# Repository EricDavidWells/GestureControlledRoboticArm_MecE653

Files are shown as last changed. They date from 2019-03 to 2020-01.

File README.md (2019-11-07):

# Realtime Force Myography
Using the gesture controlled robotic arm developed at [HACKED2019](https://github.com/MarkSherstan/HACKED2019) the project advanced to optimize a force myography (FMG) sensor and algorithm package that can be used to robustly control upper limb prosthetics in real time.

## Background
Although there are many multifunctional hands available for prosthesis use, commercial devices are unable to utilize them largely due to restricted control interfaces. Recent research has focused on improving pattern recognition algorithms to decode electromyographic signals (EMG) into multi degree of freedom movements to enable more robust control. Although results are promising in laboratory conditions, this technique has been unable to be transferred into commercial devices. This is largely due to current surface mounted EMG sensors having inherent unpredictable issues that affect the algorithm’s performance such as cross-talk, electrical interference, muscle fatigue effects, perspiration effects, and skin impedance. An alternative to this technology for use in prosthetics is force myography (FMG). This technology seeks to exploit the deformation resulting from residual muscle movement to obtain prosthesis control. This is typically done in a very similar manner to EMG; however, instead of measuring electrical activity, an array of pressure sensors wrapped around the user’s arm measures muscle deformation. The measured sensor values act as inputs into a pattern recognition algorithm to predict the desired motions from the user. An FMG sensor and algorithm package was designed and optimized to implement robust, real time control of a simulated prosthetic device. Two iterations of prototyping have been achieved, with the second design resulting in a wireless, low profile wristband containing 11 force sensitive resistors (FSR) sensors and an inertial measurement unit (IMU) capable of sampling up to 200 Hz.

## Photos
### Wireless Armband with 11 FSR's, IMU, and Custom PCB
<p align="center">


### Coordinate Frame on Arm
<p align="center">


### Gestures
<p align="center">


### Raw Signals (Left Time Series - Right Spectral Series)
<p align="center">


### Classified Signals PCA Representation 
<p align="center">


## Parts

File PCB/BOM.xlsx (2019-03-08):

Designator | Value | Manufacturer Part # | DIGI-KEY Part # | Rqd Qty | Cost / Unit | x Extra | Total Qty | Total Cost | Notes | Link
R1,R2,R3,R4,R5,R6,R7,R8 | 5.1 k | ERJ-3EKF5101V | P5.10KHCT-ND | 8 | $0.10 | 5 | 40 | $3.92 | Price Break! | https://www.digikey.ca/product-detail/en/ERJ-3EKF5101V/P5.10KHCT-ND
R9 | 1 k | ERJ-3EKF1001V | P1.00KHCT-ND | 1 | $0.10 | 10 | 10 | $0.98 | Price Break! | https://www.digikey.ca/product-detail/en/ERJ-3EKF1001V/P1.00KHCT-ND
R10 | 2 k | ERJ-3EKF2001V | P2.00KHCT-ND | 1 | $0.10 | 10 | 10 | $0.98 | Price Break! | https://www.digikey.ca/product-detail/en/ERJ-3EKF2001V/P2.00KHCT-ND
R11,R12,R13,R14,R15,R16 | 10 k | ERJ-3EKF1002V | P10.0KHCT-ND | 6 | $0.10 | 7 | 42 | $4.12 | Price Break! | https://www.digikey.ca/product-detail/en/ERJ-3EKF1002V/P10.0KHCT-ND
C1,C2,C3 | 0.1 uF | CL10B104KB8NNNC | 1276-1000-1-ND | 3 | $0.05 | 7 | 21 | $0.99 | Price Break! | https://www.digikey.ca/product-detail/en/CL10B104KB8NNNC/1276-1000-1-ND
C4 | 2.2 nF | CL10B222JB8NNNC | 1276-1987-1-ND | 1 | $0.06 | 10 | 10 | $0.60 | Price Break! | https://www.digikey.ca/product-detail/en/CL10B222JB8NNNC/1276-1987-1-ND
C5 | 10 nF | CL10B103KB8NNNC | 1276-1009-1-ND | 1 | $0.05 | 10 | 10 | $0.52 | Price Break! | https://www.digikey.ca/product-detail/en/CL10B103KB8NNNC/1276-1009-1-ND
Q1,Q2 | - | BSS138 | BSS138CT-ND | 2 | $0.40 | 5 | 10 | $3.96 | Price Break! | https://www.digikey.ca/product-detail/en/on-semiconductor/BSS138/BSS138CT-ND/244294
U1 | - | 74HC4051BQ,115 | 1727-6049-1-ND | 1 | $0.59 | 10 | 10 | $5.88 | Price Break! | https://www.digikey.ca/product-detail/en/nexperia-usa-inc/74HC4051BQ115/1727-6049-1-ND/2753885
U2 | - | MPU-6050 | 1428-1007-1-ND | 1 | $11.01 | 5 | 5 | $55.04 | Price Break! | https://www.digikey.ca/product-detail/en/tdk-invensense/MPU-6050/1428-1007-1-ND/4038010
 |  |  |  |  |  |  | Total | $76.98
Other | Qty | Cost / Unit | Total Cost | Link
MPU 6050 Breakout | 1 | $14.47 | $14.47 | https://www.digikey.ca/product-detail/en/dfrobot/SEN0142/1738-1070-ND/6588492
Stepper Motor Driver | 2 | $12.05 | $24.10 | https://www.digikey.ca/product-detail/en/trinamic-motion-control-gmbh/TMC-SILENTSTEPSTICK/1460-1159-ND/5724190
Motor Controller / PDB | 1 | $30.13 | $30.13 | https://www.digikey.ca/product-detail/en/trinamic-motion-control-gmbh/TMC2660-BOB/1460-1245-ND/8037672
 |  | Total | $68.70
$100 Free Shipping
10^-6 micro µ | 0.0022 pF
10^-9 nano n | 2.2 nF
10^-12 pico p | 2200 uF

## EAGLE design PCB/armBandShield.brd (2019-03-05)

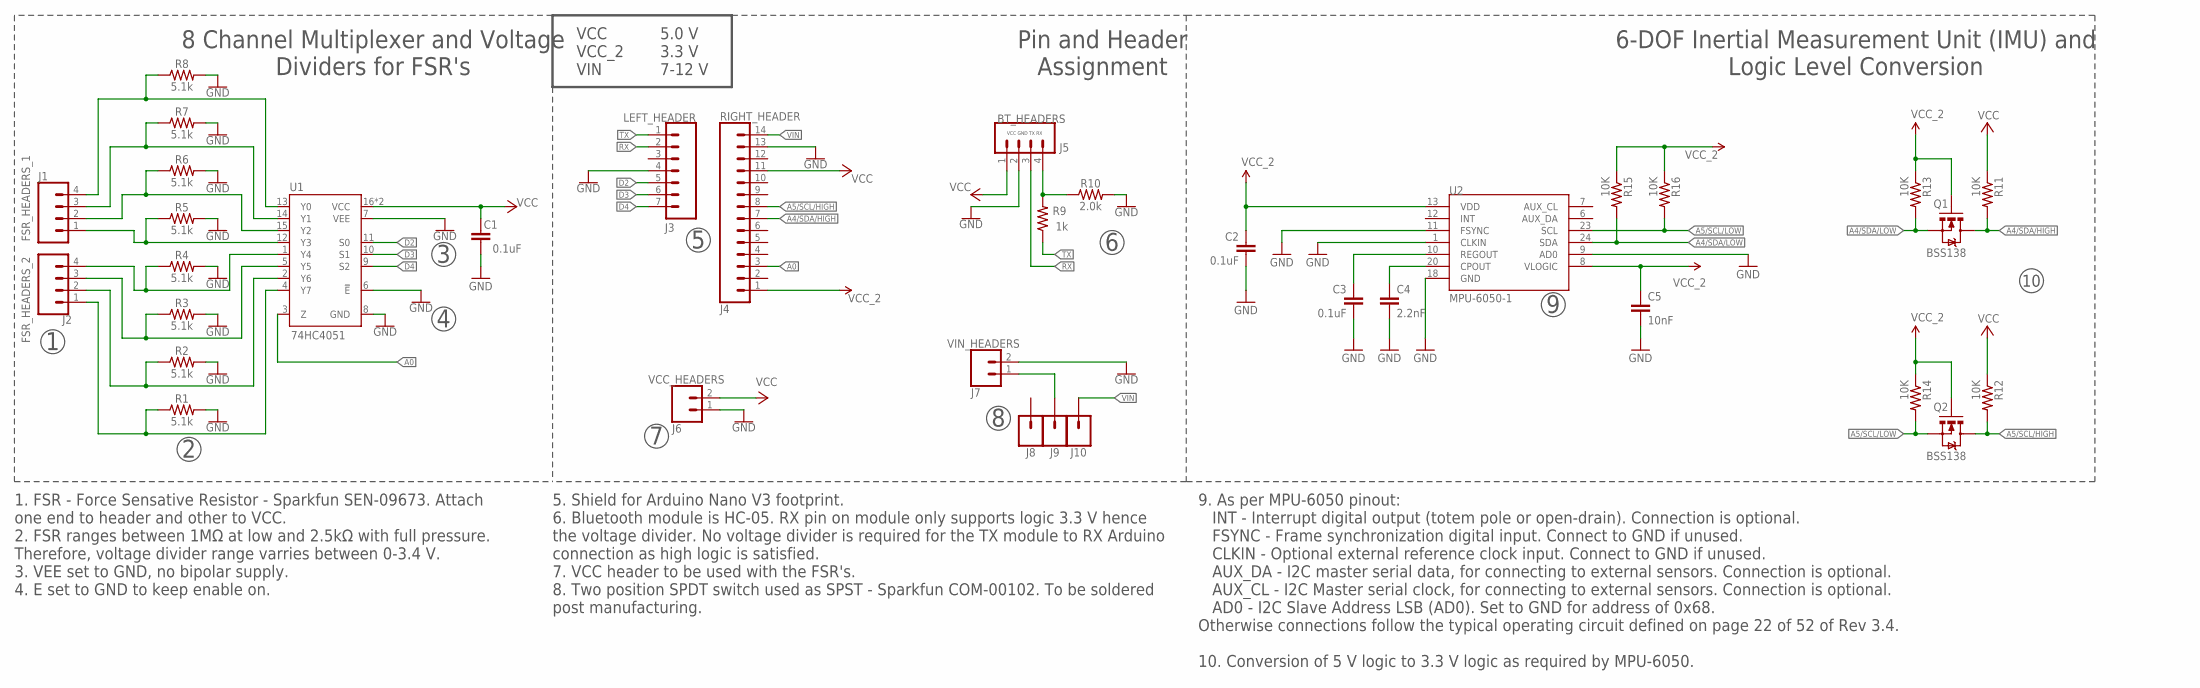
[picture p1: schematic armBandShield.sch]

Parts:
74HC4051: U1; DHVQFN-16-2.5X3.5MM
BT_HEADERS: J5; 1X04
C1, C2, C3: 0.1uF; 0603-CAP
C4: 2.2nF; 0603
C5: 10nF; 0603
J1: FSR_HEADERS_1; 1X04
J2: FSR_HEADERS_2; 1X04
J8, J9, J10: CONN_01; 1X01
LEFT_HEADER: J3; 1X07
Q1, Q2: BSS138; SOT23-3
R1, R2, R3, R4, R5, R6, R7, R8: 5.1k; 0603
R9: 1k; 0603
R10: 2.0k; 0603
R11, R12, R13, R14, R15, R16: 10K; 0603-RES
RIGHT_HEADER: J4; 1X14
U2: MPU-6050-1; QFN-24-4MM2
VCC_HEADERS: J6; 1X02_LONGPADS
VIN_HEADERS: J7; 1X02_LONGPADS

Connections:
A0: 74HC4051.3 (Z), RIGHT_HEADER.3
A4/SDA/HIGH: Q1.3 (D), R11.2, RIGHT_HEADER.7
A4/SDA/LOW: Q1.2 (S), R13.2, R15.2, U2.24 (SDA)
A5/SCL/HIGH: Q2.3 (D), R12.2, RIGHT_HEADER.8
A5/SCL/LOW: Q2.2 (S), R14.2, R16.2, U2.23 (SCL)
D2: 74HC4051.11 (S0), LEFT_HEADER.5
D3: 74HC4051.10 (S1), LEFT_HEADER.6
D4: 74HC4051.9 (S2), LEFT_HEADER.7
FSR1: 74HC4051.4 (Y7), J2.1, R1.1
FSR2: 74HC4051.2 (Y6), J2.2, R2.1
FSR3: 74HC4051.5 (Y5), J2.3, R3.1
FSR4: 74HC4051.1 (Y4), J2.4, R4.1
FSR5: 74HC4051.12 (Y3), J1.1, R5.1
FSR6: 74HC4051.15 (Y2), J1.2, R6.1
FSR7: 74HC4051.14 (Y1), J1.3, R7.1
FSR8: 74HC4051.13 (Y0), J1.4, R8.1
GND: 74HC4051.6 (!E!), 74HC4051.7 (VEE), 74HC4051.8 (GND), BT_HEADERS.2, C1.2, C2.2, C3.2, C4.2, C5.2, LEFT_HEADER.4, R1.2, R2.2, R3.2, R4.2, R5.2, R6.2, R7.2, R8.2, R10.2, RIGHT_HEADER.13, U2.1 (CLKIN), U2.9 (AD0), U2.11 (FSYNC), U2.18 (GND), VCC_HEADERS.1, VIN_HEADERS.2
unnamed: J9.1, VIN_HEADERS.1
unnamed: C4.1, U2.20 (CPOUT)
unnamed: C3.1, U2.10 (REGOUT)
unnamed: BT_HEADERS.4, R9.2, R10.1
RX: BT_HEADERS.3, LEFT_HEADER.2
TX: LEFT_HEADER.1, R9.1
VCC: 74HC4051.16 (VCC), 74HC4051.EP (VCC), BT_HEADERS.1, C1.1, R11.1, R12.1, RIGHT_HEADER.11, VCC_HEADERS.2
VCC_2: C2.1, C5.1, Q1.1 (G), Q2.1 (G), R13.1, R14.1, R15.1, R16.1, RIGHT_HEADER.1, U2.8 (VLOGIC), U2.13 (VDD)
VIN: J10.1, RIGHT_HEADER.14

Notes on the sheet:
VCC GND TX RX
8 Channel Multiplexer and Voltage Dividers for FSR's
1. FSR - Force Sensative Resistor - Sparkfun SEN-09673. Attach one end to header and other to VCC. 2. FSR ranges between 1MΩ at low and 2.5kΩ with full pressure. Therefore, voltage divider range varries between 0-3.4 V. 3. VEE set to GND, no bipolar supply. 4. E set to GND to keep enable on.
Pin and Header Assignment
6-DOF Inertial Measurement Unit (IMU) and Logic Level Conversion
5. Shield for Arduino Nano V3 footprint. 6. Bluetooth module is HC-05. RX pin on module only supports logic 3.3 V hence the voltage divider. No voltage divider is required for the TX module to RX Arduino connection as high logic is satisfied. 7. VCC header to be used with the FSR's. 8. Two position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
VCC VCC_2 VIN
5.0 V 3.3 V 7-12 V
9. As per MPU-6050 pinout: INT - Interrupt digital output (totem pole or open-drain). Connection is optional. FSYNC - Frame synchronization digital input. Connect to GND if unused. CLKIN - Optional external reference clock input. Connect to GND if unused. AUX_DA - I2C master serial data, for connec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

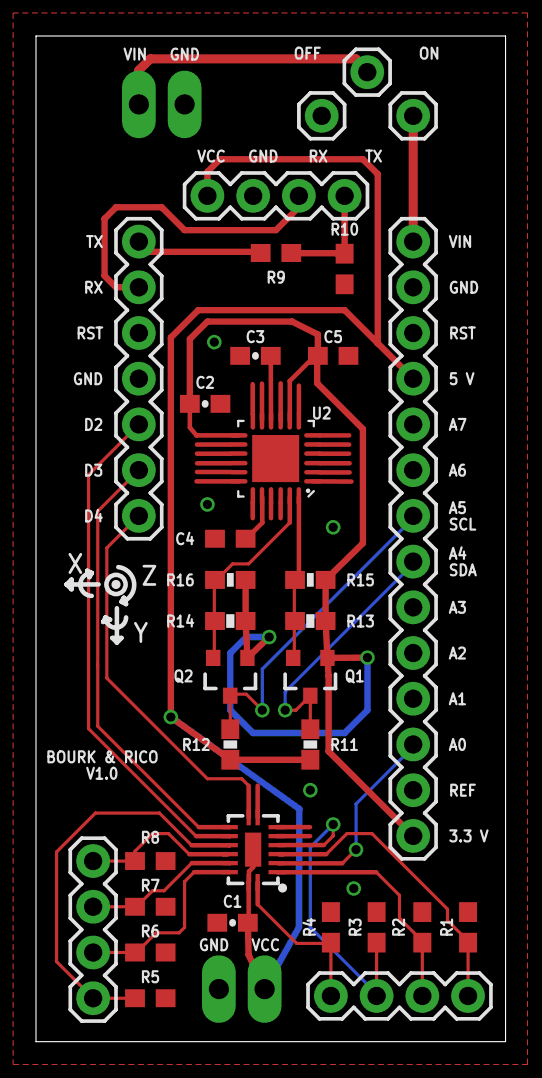
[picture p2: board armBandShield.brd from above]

Board: 2 copper layers, 26.1 x 55.9 mm, 35 parts (0 on the bottom side), 26 nets.

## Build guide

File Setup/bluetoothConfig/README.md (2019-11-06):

# Raspberry Pi 3B+ and HC-05 Set Up and Pairing

## Intro
The initial setup took a couple of hours of fiddling around with different methods and packages. The final working version was heavily based on u/Illmatic-Herbicide's [post on reddit](https://www.reddit.com/r/raspberry_pi/comments/6nchaj/guide_how_to_establish_bluetooth_serial/), however a few steps and other minor additions were made which are documented below.

The `bluetoothConfig.ino` is for setting up the HC-05 baud rate, name, etc... using AT commands. Doccumentation can be found at the begging of the sketch for proper connections, commands, etc...

## Notes
* This is specifically a headless approach and it is assumed the user has SSH'd into their Pi.
* `ratom` can be replaced by `nano` or any other text editor being used.
* When running `[bluetooth]#` enter `help` at any point for a full list of commands and explanations.
* This guide will be updated if further information is found or guidance is requested.

## Instructions
Upgrade all packages and get the required packages.
```
sudo apt-get dist-upgrade
sudo apt-get update
sudo apt-get upgrade
sudo apt-get install bluez pi-bluetooth python-bluez
```

Enter the following command for configuring Bluetooth devices (specifically on Linux).
```
bluetoothctl
```

The next 2 commands will accomplish:
1. Turn on RPi bluetooth if its not already
2. Scan for devices
```
[bluetooth]# power on
[bluetooth]# scan on
```
After waiting for a few seconds the device should be found. For example mine looked similar to this:
```
[bluetooth]#  scan on
    ...
    Device 98:D3:71:FD:61:63 Name: MECE653
    ...
```
The unique address `98:D3:71:FD:61:63` is equal to `<dev>` below. Set `<dev>` to your devices address in the remaining steps if different. Again, `<dev>` will be in the form of XX:XX:XX:XX:XX:XX.

Once your specific device has been found enter the remaining commands which do the following:
1. Stop scanning for devices
2. Enable agent with given capability
3. Pair with device. **You may need to enter a pin at this step!**
4. Trust the device
5. Connect to the device
6. Look at the device and ensure it is paired, trusted, and connected.
```
[bluetooth]# scan off
[bluetooth]# agent on
[bluetooth]# pair <dev>
[bluetooth]# trust <dev>
[bluetooth]# connect <dev>
[bluetooth]# info <dev>
```

Edit the following file using `sudo ratom /etc/systemd/system/dbus-org.bluez.service` and add "-C" to the **ExecStart** line. Then add a new line directly below it and copy and paste **ExecStartPost=/usr/bin/sdptool add SP**. The file will look something like this:

```
...
ExecStart=/usr/lib/bluetooth/bluetoothd -C
ExecStartPost=/usr/bin/sdptool add SP
...
```

Then edit the following file using `sudo ratom /etc/bluetooth/rfcomm.conf` to match the following information:
```
rfcomm1 {
    # Automatically bind the device at startup
    bind yes;

    # Bluetooth address of the device
    device <dev>;

    # RFCOMM channel for the connection
    channel 1;

    # Description of the connection
    comment "My Bluetooth Connection";
}
```

Reboot RPi using `sudo reboot` and SSH back in. Try running:

```
sudo rfcomm bind /dev/rfcomm0 <dev> 1
```

If you do not get any errors and everything checks out go ahead to `main.py` and give it a try. The Bluetooth serial port will be on `/dev/rfcomm0`.

If I missed any steps or something is not working please leave a comment or issue so that the guide can be fixed. A good resource can be found [here](https://www.raspberrypi.org/forums/viewtopic.php?t=188295).

## Update
Once everything is set up properly when logging onto the RPi simply enter the command below to activate the bluetooth serial port.

```
sudo rfcomm bind /dev/rfcomm0 98:D3:71:FD:61:63 1
```

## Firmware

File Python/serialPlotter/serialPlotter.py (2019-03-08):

# Adapted from https://www.thepoorengineer.com/en/arduino-python-plot/
from threading import Thread
import serial
import time
import collections
import matplotlib.pyplot as plt
import matplotlib.animation as animation
import struct
import copy
import pandas as pd


class serialPlot:
    def __init__(self, serialPort='/dev/cu.usbmodem14201', serialBaud=38400, plotLength=100, dataNumBytes=2, numPlots=1):
        self.port = serialPort
        self.baud = serialBaud
        self.plotMaxLength = plotLength
        self.dataNumBytes = dataNumBytes
        self.numPlots = numPlots
        self.rawData = bytearray(numPlots * dataNumBytes)
        self.dataType = None
        if dataNumBytes == 2:
            self.dataType = 'h'     # 2 byte integer
        elif dataNumBytes == 4:
            self.dataType = 'f'     # 4 byte float
        self.data = []
        for i in range(numPlots):   # give an array for each type of data and store them in a list
            self.data.append(collections.deque([0] * plotLength, maxlen=plotLength))
        self.isRun = True
        self.isReceiving = False
        self.thread = None
        self.plotTimer = 0
        self.previousTimer = 0
        # self.csvData = []

        print('Trying to connect to: ' + str(serialPort) + ' at ' + str(serialBaud) + ' BAUD.')
        try:
            self.serialConnection = serial.Serial(serialPort, serialBaud, timeout=4)
            print('Connected to ' + str(serialPort) + ' at ' + str(serialBaud) + ' BAUD.')
        except:
            print("Failed to connect with " + str(serialPort) + ' at ' + str(serialBaud) + ' BAUD.')

    def readSerialStart(self):
        if self.thread == None:
            self.thread = Thread(target=self.backgroundThread)

            self.thread.start()
            # Block till we start receiving values
            while self.isReceiving != True:
                time.sleep(0.1)

    def getSerialData(self, frame, lines, lineValueText, lineLabel, timeText):
        currentTimer = time.perf_counter()
        self.plotTimer = int((currentTimer - self.previousTimer) * 1000)     # the first reading will be erroneous
        self.previousTimer = currentTimer
        timeText.set_text('Plot Interval = ' + str(self.plotTimer) + ' ms')
        privateData = copy.deepcopy(self.rawData[:])    # so that the 3 values in our plots will be synchronized to the same sample time
        for i in range(self.numPlots):
            data = privateData[(i*self.dataNumBytes):(self.dataNumBytes + i*self.dataNumBytes)]
            value,  = struct.unpack(self.dataType, data)
            self.data[i].append(value)    # we get the latest data point and append it to our array
            lines[i].set_data(range(self.plotMaxLength), self.data[i])
            lineValueText[i].set_text('[' + lineLabel[i] + '] = ' + str(value))
        # self.csvData.append([self.data[0][-1], self.data[1][-1], self.data[2][-1]])

    def backgroundThread(self):    # retrieve data
        time.sleep(1.0)  # give some buffer time for retrieving data
        self.serialConnection.reset_input_buffer()
        self.serialConnection.timeout = 0

        # print(self.serialConnection._timeout)
        self.serialConnection.read(16*20)
        # print(self.rawData)
        self.serialConnection.timeout = None
        # print(self.serialConnection._timeout)

        while (self.isRun):
            self.serialConnection.readinto(self.rawData)
            self.isReceiving = True
            # print(self.rawData)

    def close(self):
        self.isRun = False
        self.thread.join()
        self.serialConnection.close()
        print('Disconnected...')
        # df = pd.DataFrame(self.csvData)
        # df.to_csv('../Desktop/data.csv')

å
def main():
    # portName = 'COM5'
    portName = '/dev/cu.usbmodem14201'
    baudRate = 115200
    maxPlotLength = 100     # number of points in x-axis of real time plot
    dataNumBytes = 2        # number of bytes of 1 data point
    numPlots = 8            # number of plots in 1 graph

    s = serialPlot(portName, baudRate, maxPlotLength, dataNumBytes, numPlots)
    s.readSerialStart()

    # plotting starts below
    pltInterval = 20    # Period at which the plot animation updates [ms]
    xmin = 0
    xmax = maxPlotLength
    ymin = 0
    ymax = 1024

    fig = plt.figure(figsize=(12, 6))
    ax = plt.axes(xlim=(xmin, xmax), ylim=(float(ymin - (ymax - ymin) / 10), float(ymax + (ymax - ymin) / 10)))
    ax.set_title("FSR Live Output",fontweight='bold',size=20)
    ax.set_xlabel("Time -->",fontweight='bold')
    ax.set_ylabel("Raw Analog Out",fontweight='bold')

    lineLabel = ['FSR1', 'FSR2', 'FSR3', 'FSR4', 'FSR5', 'FSR6', 'FSR7', 'FSR8']
    style = ['c-', 'm-', 'y-', '-k', '--c', '--m', '--y', '--k']
    timeText = ax.text(0.80, 0.95, '', transform=ax.transAxes)
    lines = []
    lineValueText = []
    for i in range(numPlots):
        lines.append(ax.plot([], [], style[i], label=lineLabel[i])[0])
        lineValueText.append(ax.text(0.05, 0.95-i*0.05, '', transform=ax.transAxes))

    anim = animation.FuncAnimation(fig, s.getSerialData, fargs=(lines, lineValueText, lineLabel, timeText), interval=pltInterval)    # fargs has to be a tuple

    plt.legend(loc='upper center', ncol=4)
    plt.xticks([])
    plt.show()

    s.close()


if __name__ == '__main__':
    main()

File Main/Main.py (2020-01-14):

from scipy.stats import mode
from threading import Thread
from sklearn import svm
import pandas as pd
import numpy as np
import serial
import struct
import time
import queue
import math
import pickle
import platform
import matplotlib.animation as animation


if platform.system() == "Windows":
    COMPORT = "COM16"
    import cv2
    from sklearn.decomposition import PCA
    from matplotlib import pyplot as plt
    from mpl_toolkits import mplot3d
elif platform.system() == "Darwin":
    COMPORT = "/dev/cu.MECE653-DevB"
    import cv2
    from sklearn.decomposition import PCA
    from matplotlib import pyplot as plt
    from mpl_toolkits import mplot3d
else:
    COMPORT = "/dev/rfcomm0"
    import RPi.GPIO as GPIO


class Model:
    def __init__(self, model=None):
        self.model = model
        self.trainingxdata = None
        self.trainingydata = None

    def get_training_data(self, q, data, n, classnum, trainnum):
        xdata = []
        ydata = []
        counter = 0
        for i in range(0, trainnum):
            print("Training iteration: {0}".format(i))
            for k in range(0, classnum):
                print("Class number: {0} starting in 1 second..".format(k))
                time.sleep(2)
                print("Getting data")
                # input("press enter")
                q.empty()
                for j in range(0, n):
                    data.getData(q)
                    a = [int(x) for x in data.force]
                    # b = [int(data.ax),int(data.ay),int(data.az),int(data.gx),int(data.gy),int(data.gz),int(data.dtTimer)]
                    # c = a+b
                    xdata.append(a)
                    ydata.append(k)

        self.trainingxdata = np.array(xdata)
        self.trainingydata = np.array(ydata)

    def plot_pca(self, show=True):
        self.pca = PCA(n_components=3)
        self.pca.fit(self.trainingxdata)
        Xpca = self.pca.fit_transform(self.trainingxdata)

        ax = plt.axes(projection='3d')
        for i in range(0, int(self.trainingydata.max()) + 1):
            Xtemp = Xpca[self.trainingydata == i]
            ax.scatter3D(Xtemp[:, 0], Xtemp[:, 1], Xtemp[:, 2], cmap='Greens')
            # ax.scatter3D(Xtemp[0::100][:, 0], Xtemp[0::100][:, 1], Xtemp[0::100][:, 2], cmap='Greens')
            ax.set_xlabel("PCA Axis 1")
            ax.set_ylabel("PCA Axis 2")
            ax.set_zlabel("PCA Axis 3")

        if show is True:
            plt.figure(1)
            plt.show()

    def trainSVM(self):
        self.model = svm.SVC(kernel='rbf', gamma='scale')
        self.model.fit(self.trainingxdata, self.trainingydata)

    def predict(self, data):
        prediction = self.model.predict([data])
        return prediction

    def score(self, xdata, ydata):
        score = self.model.score(xdata, ydata)
        return score

    def savemodel(self, filename):
        pickle.dump(self, open(filename, 'wb'))

    def data_split(self, p):
        """
        splits data into training and testing data by percentage p.
        :param data: ndarray of total data to be split
        :param p: percentage of data to be used for training
        :return: data split into training and testing
        """

        data = np.hstack((self.trainingxdata, np.transpose(np.array([self.trainingydata]))))
        datashuff = np.array(data)
        np.random.shuffle(datashuff)

        cutoff = int(p * data.shape[0])
        self.trainingxdata = datashuff[0:cutoff, 0:-1]
        self.trainingydata = datashuff[0:cutoff, -1]

        self.testingxdata = datashuff[cutoff::, 0:-1]
        self.testingydata = datashuff[cutoff::, -1]


class Sensors:
    def __init__(self, gyroScaleFactor, accScaleFactor, VCC, Resistor, tau):
        # Class / object / constructor setup
        self.gyroScaleFactor = gyroScaleFactor
        self.accScaleFactor = accScaleFactor
        self.VCC = VCC
        self.Resistor = Resistor
        self.tau = tau

        self.gx = None; self.gy = None; self.gz = None;
        self.ax = None; self.ay = None; self.az = None;

        self.gyroXcal = 0
        self.gyroYcal = 0
        self.gyroZcal = 0

        self.gyroRoll = 0
        self.gyroPitch = 0
        self.gyroYaw = 0

        self.roll = 0
        self.pitch = 0
        self.yaw = 0

        self.dtTimer = 0

        self.FSRvalues = []
        self.force = [0, 0, 0, 0, 0, 0, 0, 0, 0, 0, 0, 0]

    def getRawSensorValues(self, q):
        # Get raw values from serial connection
        while q.empty():
            time.sleep(0.0001)
            pass
        val = q.get(block=False)
        q.task_done()

        self.gx = val[0]
        self.gy = val[1]
        self.gz = val[2]
        self.ax = val[3]
        self.ay = val[4]
        self.az = val[5]
        self.FSRvalues = [val[6], val[7], val[8], val[9], val[10], val[11], val[12], val[13], val[14], val[15], val[16]]

    def calibrateGyro(self, s, N):
        # Display message
        print("Calibrating gyro with " + str(N) + " points. Do not move!")

        # Take N readings for each coordinate and add to itself
        for ii in range(N):
            self.getRawSensorValues(s)
            self.gyroXcal += self.gx
            self.gyroYcal += self.gy
            self.gyroZcal += self.gz

        # Find average offset value
        self.gyroXcal /= N
        self.gyroYcal /= N
        self.gyroZcal /= N

        # Display message and restart timer for comp filter
        print("Calibration complete")
        self.dtTimer = time.time()

    def processIMUvalues(self):
        # Subtract the offset calibration values
        self.gx -= self.gyroXcal
        self.gy -= self.gyroYcal
        self.gz -= self.gyroZcal

        # Convert to instantaneous degrees per second
        self.gx /= self.gyroScaleFactor
        self.gy /= self.gyroScaleFactor
        self.gz /= self.gyroScaleFactor

        # Convert to g force
        self.ax /= self.accScaleFactor
        self.ay /= self.accScaleFactor
        self.az /= self.accScaleFactor

    def compFilter(self):
        # Get the processed values from IMU
        self.processIMUvalues()

        # Get delta time and record time for next call
        dt = time.time() - self.dtTimer
        self.dtTimer = time.time()

        # Acceleration vector angle
        accPitch = math.degrees(math.atan2(self.ay, self.az))
        accRoll = math.degrees(math.atan2(self.ax, self.az))

        # Gyro integration angle
        self.gyroRoll -= self.gy * dt
        self.gyroPitch += self.gx * dt
        self.gyroYaw += self.gz * dt
        self.yaw = self.gyroYaw

        # Comp filter
        self.roll = (self.tau)*(self.roll - self.gy*dt) + (1-self.tau)*(accRoll)
        self.pitch = (self.tau)*(self.pitch + self.gx*dt) + (1-self.tau)*(accPitch)

    def processFSRvalues(self):
        # Loop through all values
        for ii in range(len(self.FSRvalues)):
            # Analog value to voltage
            fsrV = self.FSRvalues[ii] * self.VCC / 1023.0

            # Use voltage and static resistor value to calculate FSR resistance
            try:
                fsrR = ((self.VCC - fsrV) * self.Resistor) / fsrV
            except:
                fsrR = 1e6

            # Guesstimate force based on slopes in figure 3 of FSR datasheet (conductance)
            fsrG = 1.0 / fsrR

            # Break parabolic curve down into two linear slopes
            if (fsrR <= 600):
                self.force[ii] = (fsrG - 0.00075) / 0.00000032639
            else:
                self.force[ii] =  fsrG / 0.000000642857

        # Write the last entry of force to be the average value
        self.force[11] = np.mean(self.force)

    def getData(self, s):
        # Get current time
        timer = time.perf_counter()

        # Stabilize sampling rate to 200 Hz
        while (time.perf_counter() < timer + 0.005):
            pass

        # Get data from serial
        self.getRawSensorValues(s)

        # Process IMU values
        self.compFilter()

        # Process FSR values
        self.processFSRvalues()

    def logData(self, s, T):
        # Set up timer, counter, and temp data storage
        startTime = time.perf_counter()
        count = 0
        tempData = []

        # Run for T seconds
        while time.perf_counter() < startTime + T:
            self.getData(s)
            tempData.append([time.perf_counter() - startTime] + self.force + [self.roll, self.pitch, self.yaw])
            count += 1

        # Close serial connection, write data, and display sampling rate
        print("Sampling rate: ", count / (time.perf_counter() - startTime), " Hz")

        # Write data to CSV
        df = pd.DataFrame(tempData, columns=['Time', 'FSR1', 'FSR2', 'FSR3', 'FSR4', 'FSR5', 'FSR6',
                                   'FSR7', 'FSR8', 'FSR9', 'FSR10', 'FSR11', 'Avg', 'Roll', 'Pitch', 'Yaw'])

        df.to_csv('data.csv', index=None, header=True)

    def visualize(self, q, buf, T):

        global visualizedatax, visualizedatay, lines, timer

        fig = plt.figure()

        ax1 = fig.add_subplot(1, 1, 1)
        ax1.set_ylim([0, 500])
        ax1.set_xlim([0, buf])
        lines = []
        for i in range(0, 12):
            line, = (ax1.plot([], [], lw=1))
            lines.append(line)

        visualizedatax = np.arange(0, buf, 1)
        visualizedatay = np.zeros([12, buf])

        timer = time.perf_counter()

        # Get current time
        anim = animation.FuncAnimation(fig, animate, fargs=(self, q,), interval=1, blit=True)
        plt.show()

        while time.perf_counter() < timer + T:
            pass
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

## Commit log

2019-01-28 Servo kill switch, display messages, readability
2019-01-28 Added variable classes to visualize data
    [1450_fake8classes.csv]
2019-02-15 Initial commit of Eagle files
    [armBandShield.brd, armBandShield.sch]
2019-02-16 Commit robotArm printing resources
    [Part-Tracker.xlsx]
2019-02-16 Clean up schematic using labels. Remove old board. Prepare for breakout.
    [armBandShield.brd, armBandShield.sch]
2019-02-16 Added required breakout components for MPU 9250
    [armBandShield.sch]
2019-02-16 Added required breakout components for Multixplexer
    [armBandShield.sch]
2019-02-16 Initial board lay out and .brd commit
    [armBandShield.brd, armBandShield.sch]
2019-02-16 Clean up silk screen and add ground plane.
    [armBandShield.brd]
2019-02-17 Sliced remaining files and added hardware list.
    [Part-Tracker.xlsx]
2019-02-17 All connections routed
    [armBandShield.brd, armBandShield.sch]
2019-02-17 Increase solder pad lengths for chips
    [armBandShield.brd]
2019-02-17 Begin performing DRC checks
    [armBandShield.brd]
2019-02-17 Rev 1 board completed. Performed checks and added headers for switch.
    [armBandShield.brd, armBandShield.sch]
2019-02-18 Designed a board for headers / brkt board to manufacture at engg garage.
    [armBandHeaderShield.brd, armBandHeaderShield.sch]
2019-02-18 Updated print log
    [Part-Tracker.xlsx]
2019-02-19 Replace MPU-9250 with MPU-6050. Added logic level. Cleaned up schematic.
    [armBandShield.brd, armBandShield.sch]
2019-02-19 Added reference designators and double checked entire schematic.
    [armBandShield.sch]
2019-02-19 Initial layout 95% complete
    [armBandShield.brd, armBandShield.sch]
2019-02-19 Board V2 Completed.
    [armBandShield.brd, armBandShield.sch]
2019-02-19 Offset swtich headers.
    [armBandHeaderShield.brd, armBandHeaderShield.sch]
2019-02-19 Updated part tracker with all printing.
    [Part-Tracker.xlsx]
2019-02-21 Initial commit of IMU with a comp filter.
2019-02-21 Commit bluetooth AT configuration sketch with current values.
2019-03-04 Added serial to python, changed how arduino reads serial
2019-03-04 Update trace sizes, pad extensions, silkscreen, and some routing.
    [armBandShield.brd, armBandShield.sch]
2019-03-04 Double checked schematic and moved a few traces for asthetics.
    [armBandShield.brd]
2019-03-05 Increase tstop and tcream
    [armBandShield.brd]
2019-03-05 Commit Gerber files and final rev 1 of board.
    [armBandShield.brd, armBandShield.sch]
2019-03-05 Commit Gerber files and final rev 1 for the header version of board.
    [armBandHeaderShield.brd, armBandHeaderShield.sch]
2019-03-06 Got rid of threads
    Running at approximately 200 Hz
2019-03-07 Optimized the time sync for 200 Hz
2019-03-07 Comment out calibration portion
2019-03-07 Initial commit of Python script to plot angles from filter, gyro, accel
2019-03-08 Integrated serialComs into main for one way coms
    Running at 160Hz on my home pc
    [1450_RicoGrandFinalPrezMod.csv]
2019-03-08 Added shield directory
    [armBandShield.brd]
2019-03-08 create armband directory
    [FSR_Mount.SLDPRT, FSR_Mount.STL]
2019-03-08 Commit PCB BOM and add gerbers to shield folder
    [BOM.xlsx]
2019-03-08 Update BOM and data sheets
    [BOM.xlsx]
2019-03-09 Begin treansfer from Arduino to python. Wrote gyro calibration function.
2019-03-10 Added a comp filter function
2019-03-17 Add end effector CAD files.
    [Grippers.SLDPRT, Mount.SLDPRT, Pinion.SLDPRT]
2019-03-17 Add name tag and update FSR mount
    [FSR_Mount.SLDPRT, NameTag.SLDPRT]
2019-03-31 Added 3 analog pins and a couple lines to print ASCII values to serial.
2019-03-31 Send additional sensor data to Python and add footer hexadecimal bytes.
2019-03-31 Add extra FSR sensors and footer check.
2019-04-01 Commit updated armband Solidworks Files.
    [Arduino_Case.SLDPRT, Bottom Bumper.SLDPRT, FSR_Mount.SLDPRT, FSR_Mount.STL]
2019-04-05 Initial commit of a filter designer.
2019-04-06 Round print to 2 sig dig screen for FSR and angles.
2019-04-07 Added threading, trainSVM model, spaghetti
2019-04-07 Fixed sampling rate issue to confirm 200 Hz
2019-04-07 Minor filter design updates
2019-04-07 Commit some data for real time control
    [data.csv]
2019-04-07 Clean up the filtering and data writing.
2019-11-06 Remove data
    [1029_BourkFinal.csv, 1111_RicoFinal.csv, 1305_RicoFinalPrez.csv, 1450_RicoGrandFinalPrez.csv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]
2019-11-06 Remove CAD and create single PCB folder.
    [Arduino_Case.SLDPRT, BOM.xlsx, Bottom Bumper.SLDPRT, FSR_Mount.SLDPRT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]
2019-11-06 Finalized PCB directory.
    [armBandHeaderShield.brd, armBandHeaderShield.sch, armBandShield.brd, armBandShield.sch]
2019-11-07 fixed thread exiting
2020-01-14 Added realtime visualization of raw FSR values for debugging
    [data.csv]

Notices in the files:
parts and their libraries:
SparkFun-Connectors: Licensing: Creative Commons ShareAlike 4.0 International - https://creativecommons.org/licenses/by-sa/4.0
